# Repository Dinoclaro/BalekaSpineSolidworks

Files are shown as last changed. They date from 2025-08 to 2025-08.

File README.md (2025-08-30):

# Baleka Spine CAD Model

This repository contains the SolidWorks CAD model for the **Baleka Spine**.  
It is based on a modified version of the **Baleka 2.5 CAD** model, adapted for compatibility with both the new **three-degree-of-freedom (DoF) spine** and the existing **AeroDima tail**.

The Baleka Spine was developed to create a half-cheetah robotic model for studying the effect of the tail on the hindquarters during specific motions such as rapid turns. The spine integrates **three Steadywin GIM8115-6 motors** using MIT control to provide independent **roll**, **pitch**, and **yaw** actuation.  

The system is operated via **MATLAB Simulink Real-Time** on a **SpeedGoat** target computer.  

The design was created using **SolidWorks 2024 Student Edition**.  
All design calculations and resources are stored in the **BalekaSpine** folder within the NAS file system.

*Updated by Dino Claro ([clarodino@icloud.com](mailto:clarodino@icloud.com))*

## Manufacturing

- **Sheet metal parts**: Can be manufactured at Vulcan or Fabrinox. Specify required surface finishes and critical dimensions. The latest Baleka Spine assembly was manufactured at Vulcan.
- **Machined parts**: Can be produced at the Mechanical Engineering workshop.
- Refer to the **BOM** for a complete list of parts to be manufactured, 3D printed, or ordered.

## Assembly

- Refer to the **assembly instructions** doc.

## Shopping List

### 3-DOF Spine

| Part Number                                | Description                                                    | QTY | Supplier            |
|--------------------------------------------|----------------------------------------------------------------|-----|---------------------|
| BLKS-S001                                  | Heim Rod Turnbuckle                                            | 2   | Experimental Space  |
| Coiled Spring Pin Metric HD-4x35-St        | Coiled Spring Pin, Heavy Duty, 4 mm × 35 mm, Steel             | 3   | Topfast             |
| skf_bearing_6002-2rsh_2_01                 | SKF 6002-2RSH Deep Groove Ball Bearing                         | 3   | BMG                 |
| a_15_unstressed                            | 15 mm External Circlip                                         | 2   | BMG                 |
| skf_bearing_6001-2rsh_2_01                 | SKF 6001-2RSH Deep Groove Ball Bearing                         | 2   | BMG                 |
| B18.3.1M - 4 x 0.7 x 12 Hex SHCS -- 12NHX   | M4 × 12 mm Hex Socket Head Cap Screw                           | 24  | Topfast             |
| B18.3.4M - 4 x 0.7 x 8 SBHCS --N            | M4 × 8 mm Socket Button Head Cap Screw                         | 24  | Topfast             |
| AM-M4-N                                    | M4 Nyloc Nut                                                   | 38  | Topfast             |
| SHS4-8                                     | Socket Head Shoulder Screw                                     | 6   | Topfast             |
| Coiled Spring Pin Metric HD-3x28-St        | Coiled Spring Pin, Heavy Duty, 3 mm × 28 mm, Steel             | 1   | Topfast             |
| B18.3.1M - 4 x 0.7 x 30 Hex SHCS -- 20NHX   | M4 × 30 mm Hex Socket Head Cap Screw                           | 6   | Topfast             |
| skf_bearing_6003-2rsh_2_01                 | SKF 6003-2RSH Deep Groove Ball Bearing                         | 1   | BMG                 |
| B18.3.4M - 4 x 0.7 x 16 SBHCS --N           | M4 × 16 mm Socket Button Head Cap Screw                        | 3   | Topfast             |
| B18.3.1M - 4 x 0.7 x 35 Hex SHCS -- 20NHX   | M4 × 35 mm Hex Socket Head Cap Screw                           | 8   | Topfast             |
| a_17_unstressed                            | 17 mm External Circlip                                         | 1   | BMG                 |
| skf_bearing_6000-2rsh_2_01                 | SKF 6000-2RSH Deep Groove Ball Bearing                         | 2   | BMG                 |
| a_10_unstressed                            | 10 mm External Circlip                                         | 2   | BMG                 |
| B18.3.1M - 4 x 0.7 x 20 Hex SHCS -- 20NHX   | M4 × 20 mm Hex Socket Head Cap Screw                           | 3   | Topfast             |
| PHS 5 Body                                 | PHS5 Female Rod End Bearing Body                               | 4   | BMG                 |
| B18.3.1M - 5 x 0.8 x 20 Hex SHCS -- 20NHX   | M5 × 20 mm Hex Socket Head Cap Screw                           | 4   | Topfast             |
| 2020 V-Slot 3mtr Black                     | 20 × 20 mm Aluminium V-Slot Extrusion, 3 m, Black Anodised     | 4   | Moduasm             |
| T NUT PG15 PG20                            | T-Nut for 20 × 20 mm Extrusion Profile                         | 2   | Moduasm             |

---

## References

1. D. Bright, S. Shield, and A. Patel, "AeroDima: Cheetah-Inspired Aerodynamic Tail Design for Rapid Maneuverability," *2024 IEEE International Conference on Robotics and Automation (ICRA)*, Yokohama, Japan, 2024, pp. 1451–1456. [doi:10.1109/ICRA57147.2024.10610202](https://ieeexplore.ieee.org/document/10610202)  
2. C. Fischer, A. Blom, and A. Patel, “Baleka: A Bipedal Robot for Studying Rapid Maneuverability,” *Frontiers in Mechanical Engineering*, 2020. [doi:10.3389/fmech.2020.00054](https://www.frontiersin.org/articles/10.3389/fmech.2020.00054/full)

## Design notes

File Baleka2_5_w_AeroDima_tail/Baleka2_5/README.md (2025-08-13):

# Baleka 2.5 CAD Model

This is the SolidWorks CAD Model for Baleka 2.5. 

It was designed with SolidWorks 2024 Student Edition.

Updated by Matt Church

# Manufacturing + Assembly Tips
- Baleka 2.5 was originally manufactured using AL-1050 Aluminium, while structurally it is strong enough, the metal gets scuffed easily as it is softer. 
  It is recommended to use AL-5083 as it will show less visible wear and tear. 
- Plates can be manufactured at Vulcan of Fabrinox. Specify the surface finish or powder coating required.
  Needs to be collected if made at Vulcan. 
- Rear spacers are required for the motor mounting as the holes are blind, there is also not enough thread after the spacer for a 20mm M4 Cap screw to work. 
- A Half version can be made [Half_Leka]. This is created by using both outside plates and connecting them to a set of motors.

# Shopping List 

## Baleka Full 

| Item  | QTY   | Use   |
| :----- | :-----: | :----- |
| M4 x 20mm | 24 | Motor Front Mounting |
| M4 x 25mm | 24 | Motor Rear Mounting |
| M4 x 50mm | 24 | Connecting Legs to Motor |
| M5 x 14mm | 12 | Connecting top plate + Cross Braces |
| M5 x 10mm | 10 | Attaching items to Top Plate |
| M5 Nyloc | 8 | Connecting Top Plate | 

## Baleka Half [Half_Leka]

| Item  | QTY   | Use   |
| :----- | :-----: | :----- |
| M4 x 20mm | 12 | Motor Front Mounting |
| M4 x 25mm | 12 | Motor Rear Mounting |
| M4 x 50mm | 12 | Connecting Legs to Motor |
| M5 x 14mm | 8 | Connecting top plate + Cross Braces |
| M5 x 10mm | 5 | Attaching items to Top Plate |
| M5 Nyloc | 4 | Connecting Top Plate |

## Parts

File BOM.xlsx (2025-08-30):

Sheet: Supplied
 |  |  |  | BOM
 |  |  |  | Manufacturer Supplied
Part | Status | Supplier | Supplier link | Manufacturer | Part No. | Datasheet | Quantity | Price | Total Price
M5 Rod End Bearing, female, RH |  | BMG | https://bmgworld.net/bmg/en/ZAR/All-Categories/Bearings/Plain/Rod-Ends/Female-Thread/PHS-5/p/PHS%205 | IKO | PHS 5 | https://www.ikont.co.jp/global_data/download/pdf_catalog/cat5502dPHS.pdf | 4 | R 132.40 | R 529.59
5M Timing belt: 450 long, 15 wide, 90T | Ordered | RS-Components | https://za.rs-online.com/web/p/timing-belts/4750355 | Contitech | 450 5M 15 | https://docs.rs-online.com/6f9c/0900766b803c5d9d.pdf | 2 | R 264.48 | R 528.96
6001 2RS |  | BMG | https://bmgworld.net/bmg/en/ZAR/All-Categories/Bearings/Ball/Deep-Groove/Single-Row/6002-DDU/p/6002%20DDU | NSK | 6000 DDU |  | 2 | R 51.94 | R 103.88
6002 2RS |  | BMG | https://bmgworld.net/bmg/en/ZAR/All-Categories/Bearings/Ball/Deep-Groove/Single-Row/6003-DDU/p/6003%20DDU | NSK | 6002 DDU |  | 2 | R 57.54 | R 115.08
6003 2RS |  | BMG | https://bmgworld.net/bmg/en/ZAR/All-Categories/Bearings/Ball/Deep-Groove/Single-Row/6003-DDU/p/6003%20DDU | NSK | 6003 DDU |  | 2 | R 59.35 | R 118.70
Tente Swivel Castor Wheel, 40kg Capacity, 50mm Wheel |  | RS-Components | https://za.rs-online.com/web/p/castor-wheels/1721108?gb=s | Tente |  |  | 1 | R 165.05 | R 165.05
M3 Shoulder |  | Topfast |  |  |  |  | 5 | R 20.00 | R 100.00
M4 |  | Topfast |  |  |  |  | 50 | R 0.50 | R 25.00
M5 Bolts |  | Topfast |  |  |  |  | 15 | R 1.00 | R 15.00
 |  |  |  |  |  |  |  | TOTAL | R 1701.26
 | BMG
Part Name | Quantity | Price | Total
Spring Pin (3x28) | 1 | 2 | 2
Spring Pin (4x35) | 1 |  | 0
6001-2RSH | 2 | 51.94 | 103.88
6002-2RSH | 3 | 57.54 | 172.62
6000 -2RSH DGBB | 2 | 59.35 | 118.7
6003-2RSH-DGBB | 1 |  | 0
17mm Circlip | 1 |  | 0
15mm Circlip | 2 |  | 0
10mm Circlip | 2 |  | 0
M5 Rod End Bearing, Female, RH | 4 | 132.4 | 529.6
Bearing puller |  |  | 0
 |  |  | 0
 |  | TOTAL | 926.8
 | TOPFAST
Part Name | Quantity | Price | Total
Socket Head Shoulder (SHS) 4x30 | 2 | 10 | 20
Socket Head Cap Screw (SHCS) 4x12 | 24 | 2 | 48
Socket Button Head Cap Screw (SBHCS) 4x8 | 24 | 5 | 120
M4 Nut Nylock | 48 | 1 | 48
SHS 4x15 | 2 | 10 | 20
SHS 4x8 | 6 | 10 | 60
SHCS 4x30 | 6 | 5 | 30
SBHCS 4x12 | 8 | 5 | 40
SBHCS 4x16 | 3 | 5 | 15
SHCS 4x20 | 8 | 2 | 16
SHCS 4x20 | 3 | 2 | 6
loctite
2.5mm steel drill bit
Jigsaw blades
 |  | TOTAL | 423
 | Communica
lab wire <7
XT60
Soldering iron nibs
 | Mumbos
50L

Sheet: MechEng
 |  |  |  | Stress Analysis |  |  |  |  | Tolerances
Checked | Part | Quantity | Material | Yield Strength | Max Stress Expected | Safety Factor | Verification (Matlab or Solidworks) | Comments | Fits | Alignment
 | Machining
R | BLKS-M001-Diff_shaft_bearing_seat | 2 | AISI316 | 220 | 10 | 22 | SW | T_max = 25 Nm. This bearing seat experiences the largest loads. All other bearings seats assume similar stresses
R | BLKS-M002-Diff_shaft | 1 | AISI316 | 220 | 151 | 1.456953642 | Matlab | T_max = 25 Nm
R | BLKS-M003-Universal_joint_male | 1 | AL-5083-H116 | 228 | 59 | 3.86440678 | SW | T_max = 38Nm
R | BLKS-M004-Pulley_bearing_seat | 2 | ÀISI316 | 220 | 10 | 22
R | BLKS-M005-Roll_Bearing_6003 | 1 | AISI316 | 220 | 10 | 22
R | BLKS-M006-Roll_bearing_6002 | 1 | AISI316 | 220 | 10 | 22
R | BLKS-M007-Roll-Motor-Couple | 1 | AISI316 | 220 | N/A | 2.7 | SW | Assumes transmits torque like a key and is limited by shear strength. See Matlab script
Y | BLKS-M008-Universal_joint_female | 1 | AL-5083-H116 | 228 | 198 | 1.151515152 | Matlab | T_max = 38Nm. This applies a somewhat arbitrary shear stress concentration factor to account for the step introduced by the D-section and stresses are likely to be lower.
R | BLKS_M009-Universal_joint_shaft | 1 | AISI316 | 220 | 111 | 1.981981982 | Matlab | T_max = 38Nm

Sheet: Combined
PART NUMBER | DESCRIPTION | QTY | SUPPLIER | STATUS | STRESS |  |  |  | MATERIAL | PRICE (QTY X PPU) | COMMENTS
 |  |  |  |  | MAX STRESS | YIELD STRESS | SAFETY FACTOR | SOURCE
Manufactured
BLKS-M001 | DIff Shaft Bearing Seat | 2 | MechEng | A | 10 | 220 | 22.00 | SW | AISI316 |  |  | R | Ready, needs to be checked | RED
BLKS-M002 | Diff_shaft | 1 | MechEng | A | 151 | 220 | 1.46 | Matlab, Macsteel | AISI-316 |  |  | C | Checked | GREEN
BLKS-M003 | Universal Joint Male | 1 | MechEng | A | 59 | 250 | 4.24 | SW | AL6082 |  |  | O | Ordered | BLUE
BLKS-M004 | Pulley Bearing Seat | 2 | MechEng | A | 10 | 220 | 22.00 | SW | AISI-316 |  |  | A | Arrived | YELLOW
BLKS-M005 | Roll 6003 Seat | 1 | MechEng | A | 10 | 220 | 22.00 | SW | AISI-316
BLKS-M006 | Roll 6002 Bearing Seat | 1 | MechEng | A | 10 | 220 | 22.00 | SW | AISI-316
BLKS-M007 | Roll Motor Couple | 1 | MechEng | A | 140 | 220 | 1.57 | SW | AISI-316
BLKS-M008 | Universal Joint Female | 1 | MechEng | A | 198 | 250 | 1.26 | Matlab | AL6082
BLKS-M009 | Universal Joint Shaft | 1 | MechEng | A | 111 | 220 | 1.98 | Matlab | AISI-316
 |  |  |  |  |  |  |  |  |  | 0
Sheet Metal
BLKS-SM001 | Diff back plate | 1 | Vulcan | A |  |  |  |  | AL5182 |  | Check Surface finish, bend radius, material. Change 6mm to 5.8
BLKS-SM002 | Differential Side Plate Left Rib | 1 | Vulcan | A |  |  |  |  | AL5182
BLKS-SM003 | Diff Side Plate Shaft Right Rib | 1 | Vulcan | A |  |  |  |  | AL5182
BLKS-SM004 | Control Arm w Slot | 2 | Fabrinox | A |  |  |  |  | AL6082
BLKS-SM005 | Roll Plate | 1 | Vulcan | A |  |  |  |  | AL5182
BLKS-SM006 | Roll U-Plate | 1 | Vulcan | A |  |  |  |  | AL5182
BLKS-SM007 | Roll Support Plate | 1 | Vulcan | A |  |  |  |  | AL5182
BLKS-SM008 | Jockey Plate | 1 | Vulcan | A |  |  |  |  | AL5182
BLKS-SM009 | Differential Body Rib | 1 | Vulcan | O |  |  |  |  | AL5182
BLKS-SM010 | Roll Plate Frame | 1 | Vulcan | A |  |  |  |  | Stainless Steel
BLKS-SM011 | Motor Guard | 1 | Vulcan | A |  |  |  |  | AL5182
BLKS-SM012 | Tail Pitch Back | 1 | Vulcan | A |  |  |  |  | AL5182
BLKS-SM013 | Tail Pitch Front | 1 | Vulcan | A |  |  |  |  | AL5182
BLKS-SM014 | Tail Roll | 1 | Vulcan | A |  |  |  |  | AL5182
BLK-001 | Top Plate | 1 | Vulcan | A |  |  |  |  | Al5182 |  | 4mm thickness
 |  |  |  |  |  |  |  |  |  | 0
Printing
BLKS-P001 | Differential Shaft Pulley (PT-48T- 5M-15W-12B) | 2 |  |  |  |  |  |  | PLA
BLKS-P002 | Diff Motor Pulley (-PT-48T- 15W-12B) | 2 |  |  |  |  |  |  | PLA
BLKS-P003 | Universal Joint Rod End | 1 |  |  |  |  |  |  | PA-CF
BLKS-P004 | Control Rod End Back | 2 |  |  |  |  |  |  | PA-CF
BLKS-P005 | Control Rod End Front | 2 |  |  |  |  |  |  | PA-CF
BLKS-P007 | Roll Motor Spacer | 1 |  |  |  |  |  |  | PLA
BLKS-P008 | Tail Pitch Spacer | 1 |  |  |  |  |  |  | PLA
Supplied
BLKS-S001 | Heim Rod Turnbuckle | 2 | Experimental space | A |  |  |  |  |  | 0 | Found in experimental space
Coiled Spring Pin Metric HD-4x35-St | Coiled Spring Pin, Heavy Duty, 4 mm x 35 mm, Steel | 3 | Topfast | A |  |  |  |  |  | 8.88
skf_bearing_6002- 2rsh_2_01 | SKF 6002-2RSH Deep Groove Ball Bearing | 3 | BMG | A
a_15_unstressed | 15mm External Circlip | 2 | BMG | A
skf_bearing_6001- 2rsh_2_01 | SKF 6001-2RSH Deep Groove Ball Bearing | 2 | BMG | A
B18.3.1M - 4 x 0.7 x 12 Hex SHCS -- 12NHX | M4 x 12 mm Hex Socket Head Cap Screw | 24 | Topfast | A |  |  |  |  |  | 26.91
B18.3.4M - 4 x 0.7 x 8 SBHCS --N | M4 x 8 mm Socket Button Head Cap Screw | 24 | Topfast | A |  |  |  |  |  | 63.84
AM-M4-N | M4 Aluminium Spacer/Nut | 38 | Topfast | A |  |  |  |  |  | 41.42
SHS4-8 | Socket Head Shoulder Screw | 6 | Topfast | A
Coiled Spring Pin Metric HD-3x28-St | Coiled Spring Pin, Heavy Duty, 3 mm x 28 mm, Steel | 1 | Topfast | A |  |  |  |  |  | 2.28
B18.3.1M - 4 x 0.7 x 30 Hex SHCS -- 20NHX | M4 x 30 mm Hex Socket Head Cap Screw | 6 | Topfast | A
skf_bearing_6003- 2rsh_2_01 | SKF 6003-2RSH Deep Groove Ball Bearing | 1 | BMG | A
B18.3.4M - 4 x 0.7 x 16 SBHCS --N | M4 x 16 mm Socket Button Head Cap Screw | 3 | Topfast | A
B18.3.1M - 4 x 0.7 x 35 Hex SHCS -- 20NHX | M4 x 35 mm Hex Socket Head Cap Screw | 8 | Topfast | A
a_17_unstressed | 17mm External Circlip | 1 | BMG | A
skf_bearing_6000- 2rsh_2_01 | SKF 6000-2RSH Deep Groove Ball Bearing | 2 | BMG | A
a_10_unstressed | 10mm External Circlip | 2 | BMG | A
B18.3.1M - 4 x 0.7 x 20 Hex SHCS -- 20NHX | M4 x 20 mm Hex Socket Head Cap Screw | 3 | Topfast | A
PHS 5 Body | PHS5 Female Rod End Bearing Body | 4 | BMG | A
B18.3.1M - 5 x 0.8 x 20 Hex SHCS -- 20NHX | M5 x 20 mm Hex Socket Head Cap Screw | 4 | Topfast | A
2020 V-Slot 3mtr Black | 20x20 Aluminium V-Slot Extrusion, 3 m, Black Anodised | 4 | Moduasm | A |  |  |  |  |  | 143.33
T NUT PG15 PG20 | T-Nut for 20x20 Extrusion Profile | 2 | Moduasm | A

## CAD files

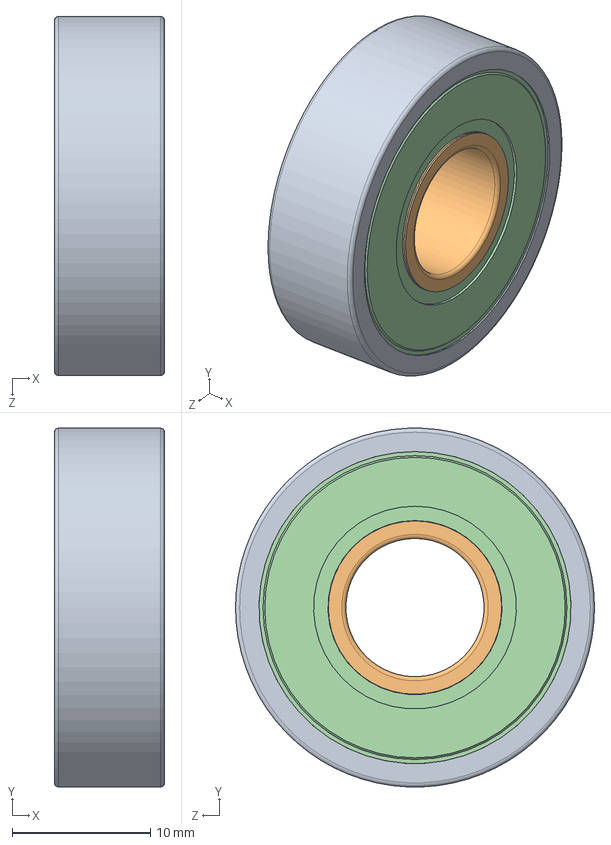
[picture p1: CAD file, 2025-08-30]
Supplied/skf_bearing_6000-2rsh_2/skf_bearing_6000-2rsh_2.SLDASM
8.00 x 26.0 x 26.0 mm
skf_bearing_6000-2rsh_2_01
skf_bearing_6000-2rsh_2_02
skf_bearing_6000-2rsh_2_03
skf_bearing_6000-2rsh_2_04
skf_bearing_6000-2rsh_2_05

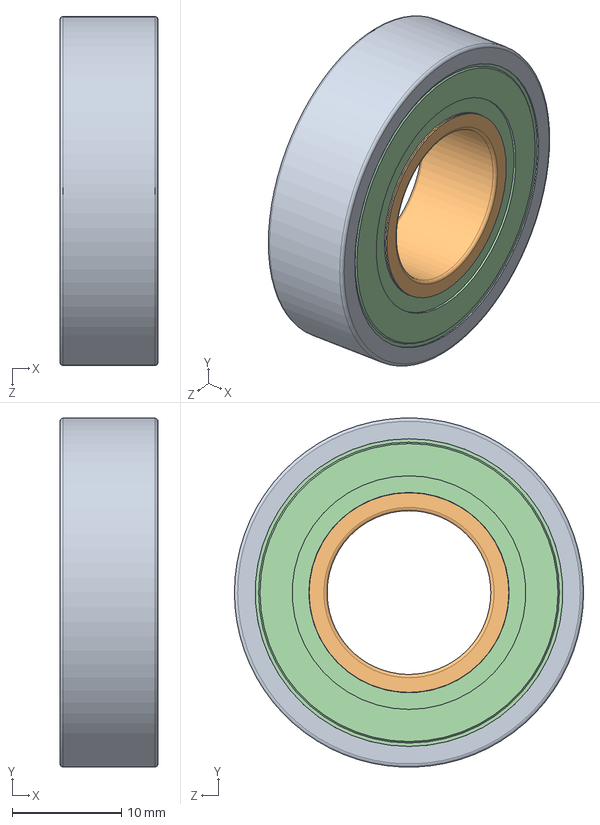
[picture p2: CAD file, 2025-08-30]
Supplied/skf_bearing_6002-2rsh_2/skf_bearing_6002-2rsh_2.SLDASM
9.00 x 32.0 x 32.0 mm
skf_bearing_6002-2rsh_2_01
skf_bearing_6002-2rsh_2_02
skf_bearing_6002-2rsh_2_03
skf_bearing_6002-2rsh_2_04
skf_bearing_6002-2rsh_2_05

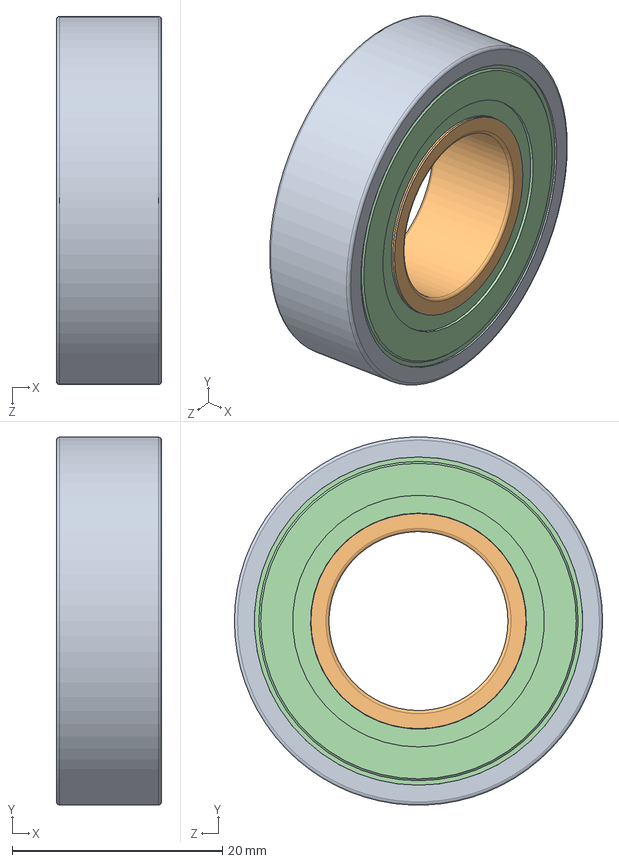
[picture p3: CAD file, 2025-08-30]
Supplied/skf_bearing_6003-2rsh_2/skf_bearing_6003-2rsh_2.SLDASM
10.0 x 35.0 x 35.0 mm
skf_bearing_6003-2rsh_2_01
skf_bearing_6003-2rsh_2_02
skf_bearing_6003-2rsh_2_03
skf_bearing_6003-2rsh_2_04
skf_bearing_6003-2rsh_2_05

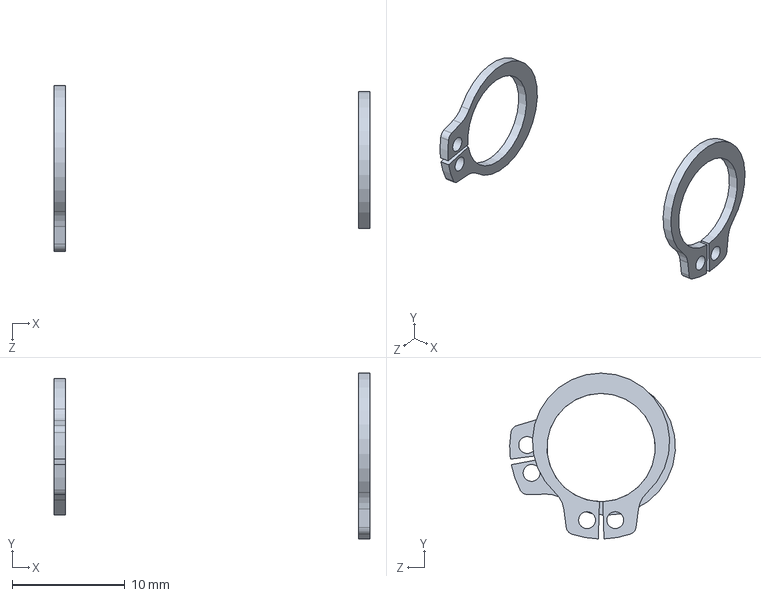
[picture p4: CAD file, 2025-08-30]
Baleka2_5_w_AeroDima_tail/Baleka2_5/Sub_Assemblies/AssemblyFootV2 BALEKA II .SLDASM
28.0 x 14.7 x 14.7 mm
circlip for shafts normal_din x 2

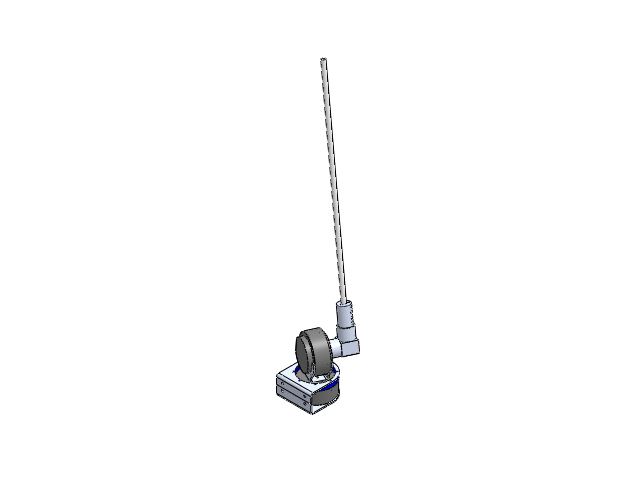
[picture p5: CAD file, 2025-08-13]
Baleka2_5_w_AeroDima_tail/Aero-dima_tail/Tail_assem.SLDASM
BLKS-SM012-tail-pitch-back
ak70-10 x 2
BLKS-SM014-tail_roll
roll spacer
tail_interface
carbon fiber tail
shaft coupler
BLKS-SM013-tail-pitch-front
BLKS-P008-tail-pitch-spacer

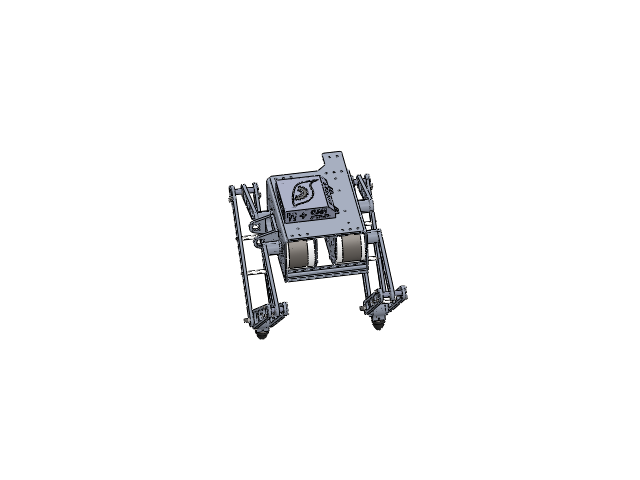
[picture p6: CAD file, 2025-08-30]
Baleka2_5_w_AeroDima_tail/Baleka2_5/Baleka2_5.SLDASM
AK10-9 KV60 V3.0 x 4
B2.5 Inner Shield Plate x 2
B2.5 Outer Shield Plate x 2
adapted_ring x 4
rear_ring x 4
rear_M4_spacer x 24
BLK001-top_plate
cross_brace x 2
Gland x 2
01-013 robot_mount_fixed
BLK2-002 Upper Leg Link New BALEKA II x 4
_6900_Outer_ring_2 BALEKA II x 12
_6900_Inner_ring_4 BALEKA II x 12
_6900_Ball_6 BALEKA II x 120
circlip for shafts normal_din x 20
BLK010 Middle Leg Joint Shaft New BALEKA II x 4
BLK009 Bearing Locator New BALEKA II x 8
socket head cap screw_iso x 16
BLK2-001 Upper Leg Coupler BALEKA II x 4
BLK2-003 Left Lower Leg Plated BALEKA II x 4
Lower Leg Compression Coupler BALEKA II x 8
BLK2-009 Inner Leg Pin BALEKA II x 8
plain washer 10673 type snl_iso x 16
hex thin nut gradeb_iso x 16
BLK2-004 Right Lower Leg Plated BALEKA II x 4
Spacer Lower Legs Link BALEKA II x 4
FootBlockDoubleBearing BALEKA II x 2
FootShaft BALEKA II x 2
FootRubber BALEKA II x 2
Baleka Lid v3.step
Leg_mount_spacer x 4
Cable_Bulkhead_mod

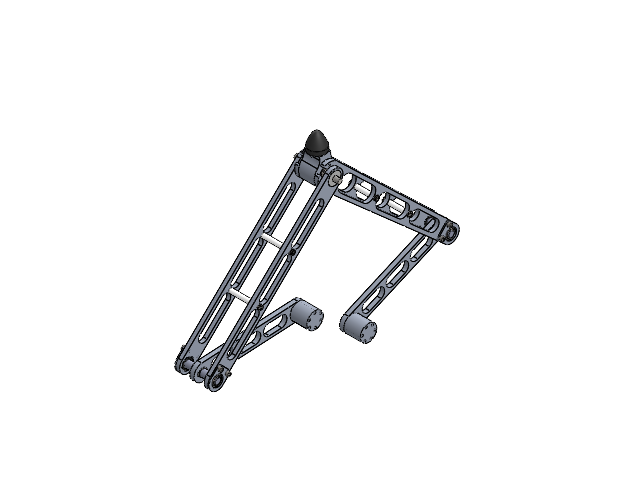
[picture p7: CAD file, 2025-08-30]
Baleka2_5_w_AeroDima_tail/Baleka2_5/Sub_Assemblies/Leg_pair.SLDASM
BLK2-002 Upper Leg Link New BALEKA II x 2
_6900_Outer_ring_2 BALEKA II x 6
_6900_Inner_ring_4 BALEKA II x 6
_6900_Ball_6 BALEKA II x 60
circlip for shafts normal_din x 10
BLK010 Middle Leg Joint Shaft New BALEKA II x 2
BLK009 Bearing Locator New BALEKA II x 4
socket head cap screw_iso x 8
BLK2-001 Upper Leg Coupler BALEKA II x 2
BLK2-003 Left Lower Leg Plated BALEKA II x 2
Lower Leg Compression Coupler BALEKA II x 4
BLK2-009 Inner Leg Pin BALEKA II x 4
plain washer 10673 type snl_iso x 8
hex thin nut gradeb_iso x 8
BLK2-004 Right Lower Leg Plated BALEKA II x 2
Spacer Lower Legs Link BALEKA II x 2
FootBlockDoubleBearing BALEKA II
FootShaft BALEKA II
FootRubber BALEKA II

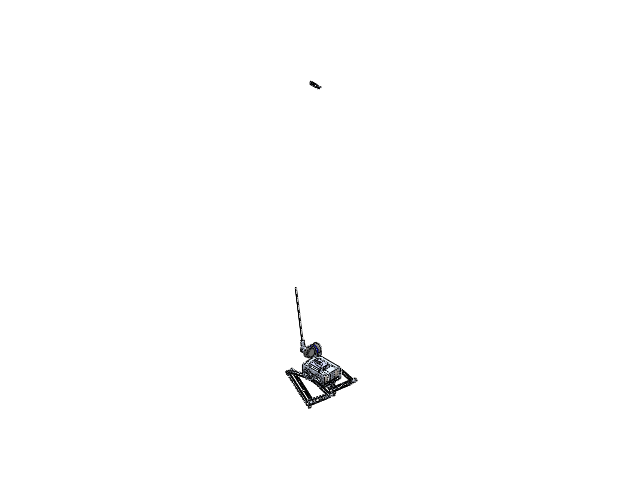
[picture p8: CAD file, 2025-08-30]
Baleka2_5_w_AeroDima_tail/baleka2_5_w_AeroDima_Tail.SLDASM
AK10-9 KV60 V3.0 x 4
B2.5 Inner Shield Plate x 2
B2.5 Outer Shield Plate x 2
adapted_ring x 4
rear_ring x 4
rear_M4_spacer x 24
BLK001-top_plate
cross_brace x 2
Gland x 2
01-013 robot_mount_fixed
BLK2-002 Upper Leg Link New BALEKA II x 4
_6900_Outer_ring_2 BALEKA II x 12
_6900_Inner_ring_4 BALEKA II x 12
_6900_Ball_6 BALEKA II x 120
circlip for shafts normal_din x 20
BLK010 Middle Leg Joint Shaft New BALEKA II x 4
BLK009 Bearing Locator New BALEKA II x 8
socket head cap screw_iso x 16
BLK2-001 Upper Leg Coupler BALEKA II x 4
BLK2-003 Left Lower Leg Plated BALEKA II x 4
Lower Leg Compression Coupler BALEKA II x 8
BLK2-009 Inner Leg Pin BALEKA II x 8
plain washer 10673 type snl_iso x 16
hex thin nut gradeb_iso x 16
BLK2-004 Right Lower Leg Plated BALEKA II x 4
Spacer Lower Legs Link BALEKA II x 4
FootBlockDoubleBearing BALEKA II x 2
FootShaft BALEKA II x 2
FootRubber BALEKA II x 2
Baleka Lid v3.step
Leg_mount_spacer x 4
Cable_Bulkhead_mod
BLKS-SM012-tail-pitch-back
ak70-10 x 2
BLKS-SM014-tail_roll
roll spacer
tail_interface
carbon fiber tail
shaft coupler
BLKS-SM013-tail-pitch-front
BLKS-P008-tail-pitch-spacer
PG20_Drop_Nut x 2
BLKS-P011-Back_plate_spacer x 2

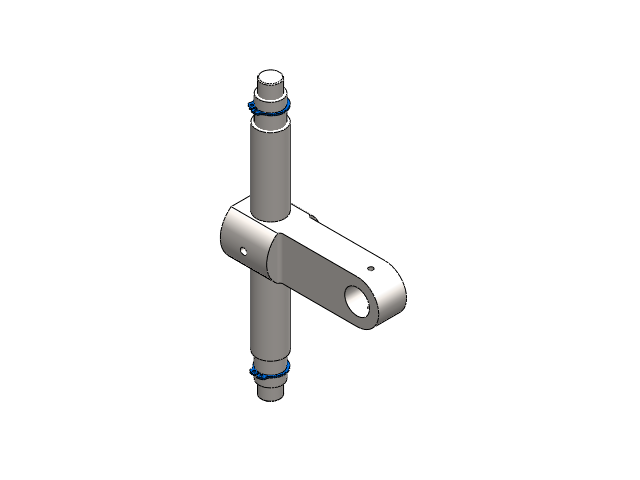
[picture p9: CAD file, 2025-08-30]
Sub-assemblies/diff_shaft_comp.SLDASM
BLKS-M002-diff_shaft
BLKS-M003-universal_joint_male
a_15_unstressed x 2

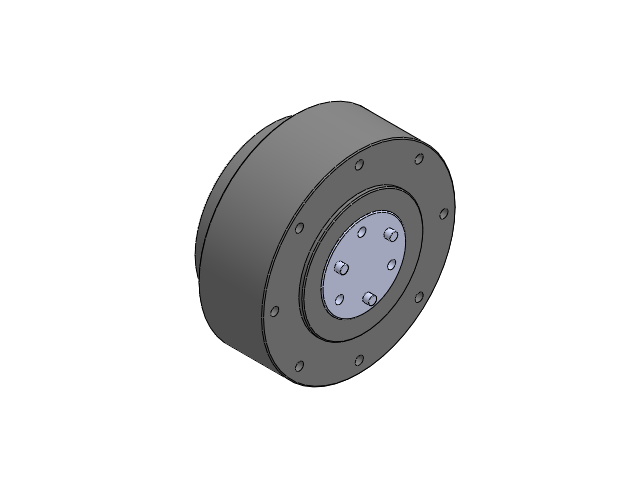
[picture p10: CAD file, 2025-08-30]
Supplied/GIM8115-6/motor_assem/motor_assem.SLDASM
motor_back_case
motor_shaft

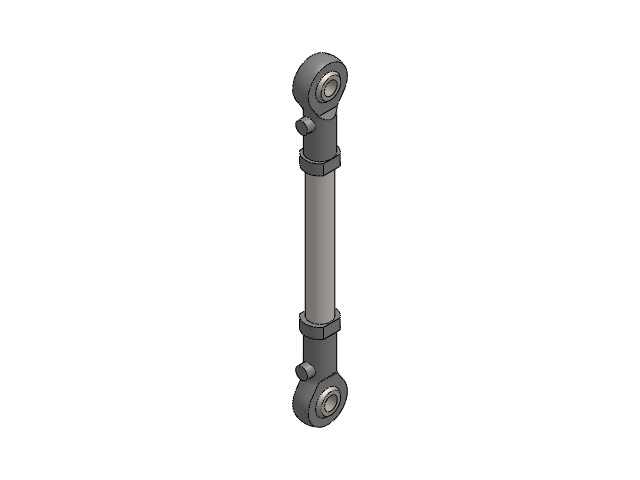
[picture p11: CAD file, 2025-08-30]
Supplied/Heim rod/heim_rod_assem.SLDASM
BLKS-S001-heim_rod_turnbuckle
PHS 5 BALL Copy x 2
PHS 5 Body x 2

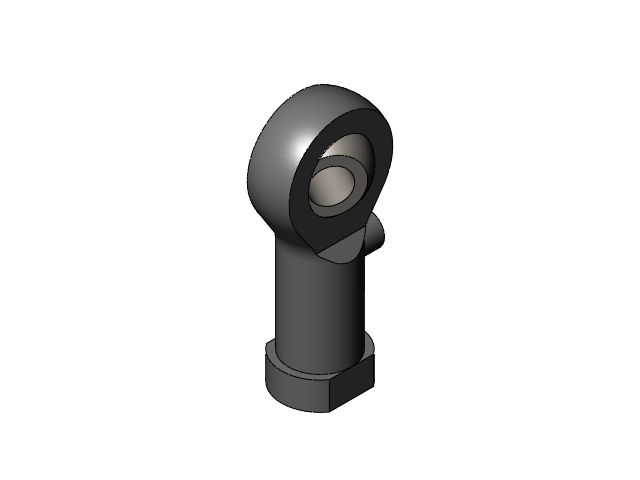
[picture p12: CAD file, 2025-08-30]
Supplied/IKO_PHS5A/SOLIDWORKS/PHS5A.sldasm
PHS 5 BALL Copy
PHS 5 Body

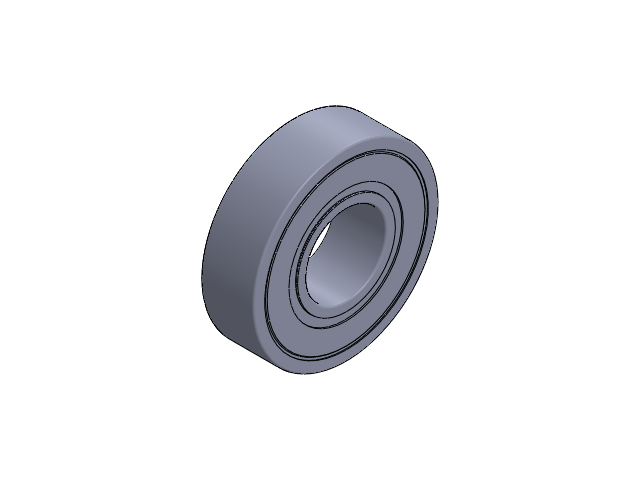
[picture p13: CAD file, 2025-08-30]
Supplied/skf_bearing_6001-2rsh_2/skf_bearing_6001-2rsh_2.SLDASM
skf_bearing_6001-2rsh_2_01
skf_bearing_6001-2rsh_2_02
skf_bearing_6001-2rsh_2_03
skf_bearing_6001-2rsh_2_04
skf_bearing_6001-2rsh_2_05

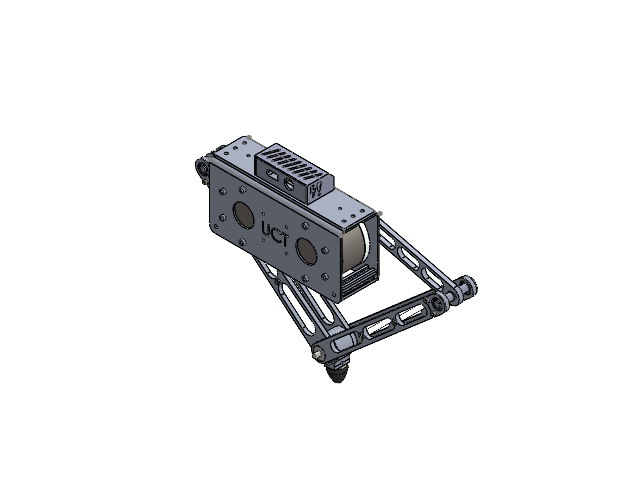
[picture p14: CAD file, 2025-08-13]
Baleka2_5_w_AeroDima_tail/Baleka2_5/Half_leka.SLDASM
adapted_ring x 2
AK10-9 KV60 V3.0 x 2
B2.5 Outer Shield Plate x 2
rear_ring x 2
Top_plate_half
BLK2-002 Upper Leg Link New BALEKA II x 2
_6900_Outer_ring_2 BALEKA II x 6
_6900_Inner_ring_4 BALEKA II x 6
_6900_Ball_6 BALEKA II x 60
circlip for shafts normal_din x 10
BLK010 Middle Leg Joint Shaft New BALEKA II x 2
BLK009 Bearing Locator New BALEKA II x 4
socket head cap screw_iso x 8
BLK2-001 Upper Leg Coupler BALEKA II x 2
BLK2-003 Left Lower Leg Plated BALEKA II x 2
Lower Leg Compression Coupler BALEKA II x 4
BLK2-009 Inner Leg Pin BALEKA II x 4
plain washer 10673 type snl_iso x 8
hex thin nut gradeb_iso x 8
BLK2-004 Right Lower Leg Plated BALEKA II x 2
Spacer Lower Legs Link BALEKA II x 2
FootBlockDoubleBearing BALEKA II
FootShaft BALEKA II
FootRubber BALEKA II
Cable_Bulkhead
Half-leka lid
cross_brace_half_leka x 2
rear_M4_spacer x 8

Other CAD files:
Baleka2_5_w_AeroDima_tail/Baleka2_5/Sub_Assemblies/Baleka_half.SLDASM
Sub-assemblies/eccentric_pulley_assem.SLDASM
Baleka2_5_w_AeroDima_tail/Baleka2_5/Sub_Assemblies/6900 BALEKA II .SLDASM
Sub-assemblies/diff_pulley_left_assem.SLDASM
Baleka2_5_w_AeroDima_tail/Aero-dima_tail/BLKS-P008-tail-pitch-spacer.SLDPRT
Baleka2_5_w_AeroDima_tail/Aero-dima_tail/BLKS-SM012-tail-pitch-back.SLDPRT
Baleka2_5_w_AeroDima_tail/Aero-dima_tail/BLKS-SM013-tail-pitch-front.SLDPRT
Baleka2_5_w_AeroDima_tail/Aero-dima_tail/BLKS-SM014-tail_roll.SLDPRT
Baleka2_5_w_AeroDima_tail/Aero-dima_tail/carbon fiber tail.SLDPRT
Baleka2_5_w_AeroDima_tail/Aero-dima_tail/roll spacer.SLDPRT
Baleka2_5_w_AeroDima_tail/Aero-dima_tail/shaft coupler.SLDPRT
Baleka2_5_w_AeroDima_tail/Aero-dima_tail/tail_interface.SLDPRT
Baleka2_5_w_AeroDima_tail/Baleka2_5/Drawings/B2.5 Inner Shield Plate.SLDDRW
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

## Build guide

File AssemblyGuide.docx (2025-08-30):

# Baleka Spine V1 Assembly Guide

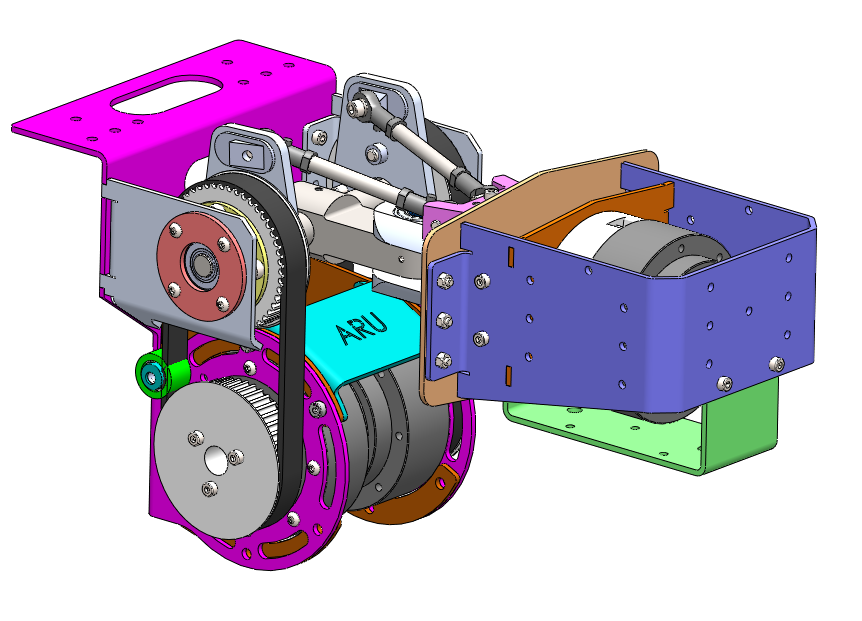
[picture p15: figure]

Updated by Dino Claro (26 August 2025)

All parts for the Spine, including the wiring harness, can be found in the project box. This guide aids with assembling the Spine and attaching it to Baleka and the frame. A brief explanation of the wiring harness is also provided. The guide primarily shows the order of assembly, and it is recommended to have the Solidworks model open alongside.

The procedure for assembling the parts that require press fits, such as the universal joint and bearings seats, is not shown here since they are already assembled and should not be taken apart unless a part has failed.

Assembly Tips:

- Washers are not shown in this guide. The general rule of thumb is to put the washer on the side that is turning. Depending on the access to the part this may either be the nut or the bolt head.
- When there are multiple screws/bolts, first tighten gently by hand and then tighten each bolt/screw by alternating to opposite sides.
- Nylock nuts are to be used throughout the assembly

## Differential Drive

### Control Arm Assembly

There are two Control-arm assemblies for the left and right Heim-rods, respectively.

Left and Right Control Assembly

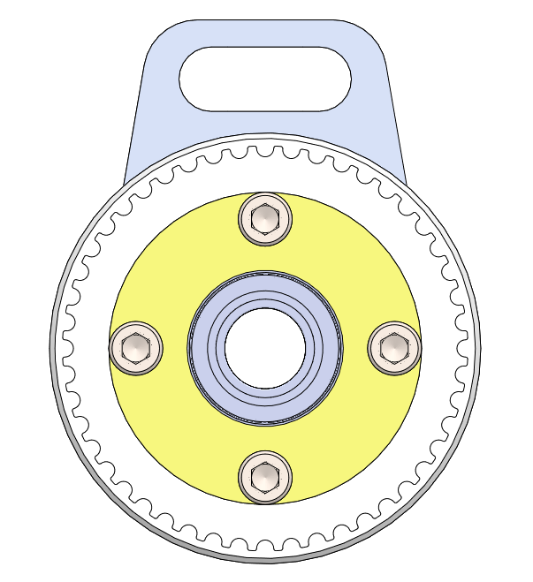
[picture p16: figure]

1. The 6002-Bearing Seat (BLKS-M004) slots into the cavity of the Differential Shaft Pulley (BLKS-P001) and is fastened with M6x30 shoulder screws and 3D printed washers (BLKS-P007).
2. Repeat for the other side.

### Differential Shaft

1. Fix the left and right control assemblies with 15mm circlips.

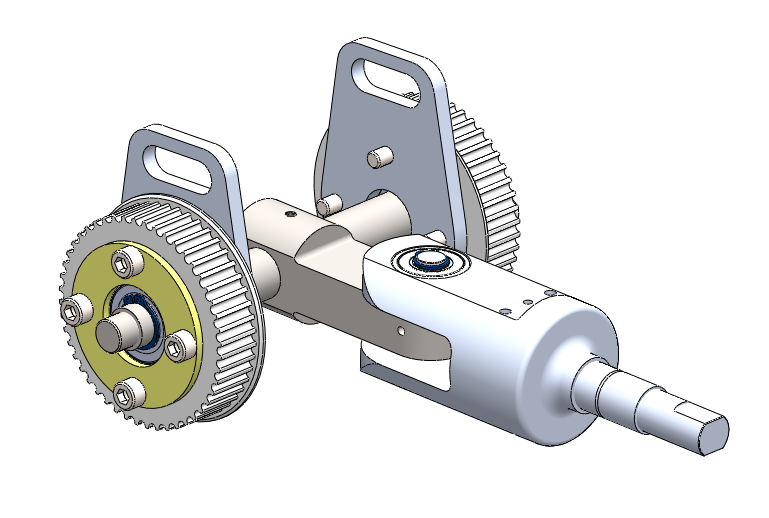
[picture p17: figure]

## Differential Drive Body

1. Attach the 6001-Bearing seat (BLKS-M001) to the side plates (BLKS-SM002 and BLKS-SM003) using M4x8 Button head screws. These screw directly into the side plates.
2. Fix the right-side Differential plate (BLKS-SM003) to the Differential back plate (BLKS-SM001) using M4x12 socket head cap screws.

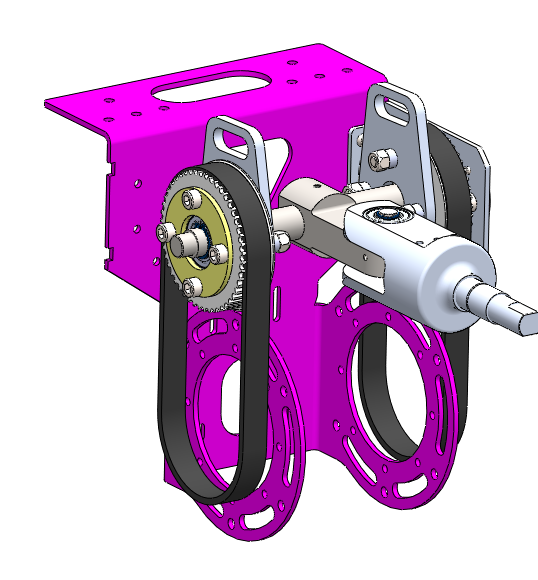
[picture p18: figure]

3. Manoeuvre the complete Differential Shaft assembly into the bearing of the right-side Differential plate. N.B. Timing belts should be placed on the pulleys at this point.

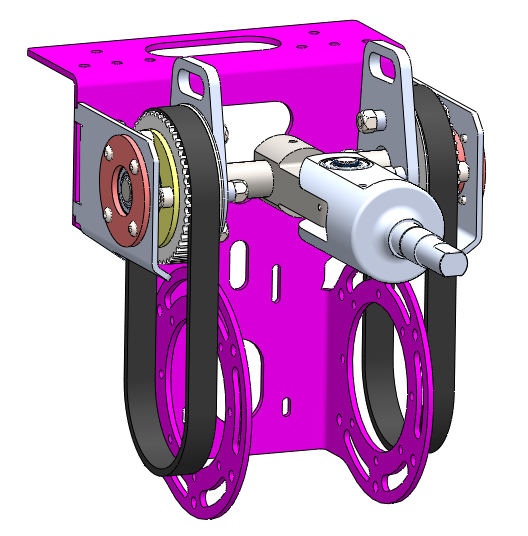
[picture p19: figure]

4. Slide the left-side Differential plate (BLKS-SM002) onto Differential Shaft and fix using M4x12 bolts. Take note of the bolt orientation for the left-side Differential plate in the image below. You should use a spanner to hold the nut and then tighten using the head of the bolt. The right-side bolt and nut can be in any orientation.
5. Place the Differential rib (BLKS-SM009) in-between the side plates of the Differential back plate (BLKS-SM001). The Differential Rib is fixed to the sides of Back-plate with M6x8 shoulder bolts.

Can included now for alignment but will have to be removed at a later stage when attaching Spine to Baleka

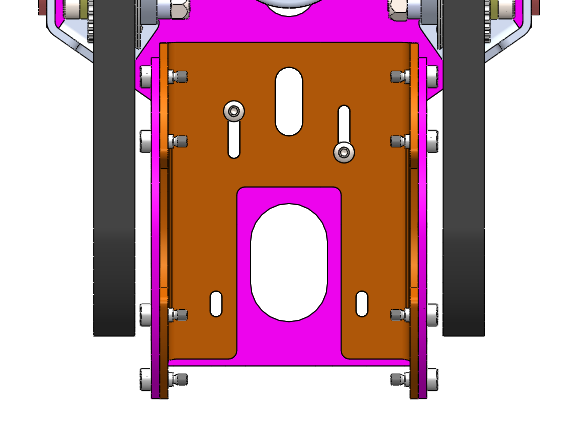
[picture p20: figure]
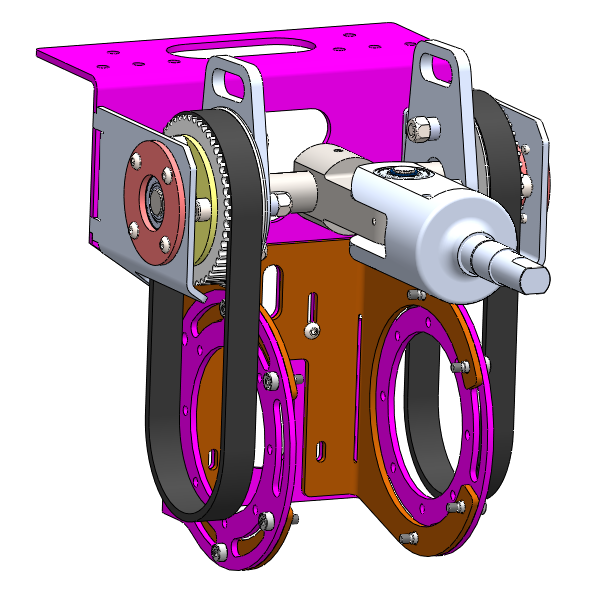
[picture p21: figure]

6. The Eccentric Belt Pulley tensioners are put together using various 3D printed parts (BLKS-P008, BLKS-P009 and BLKS-P010) as well as a 6800 DGBB. The tensioner assembly is attached to the Differential body using M6x35mm bolt and nut. Note: There may not be a hole in the Differential Rib. This is because the hole is too close to the bend line and must be drilled after receiving from Vulcan Steel. Insert the other shoulder bolts and mark the position with a drill punch to achieve correct hole location.

## Roll Body

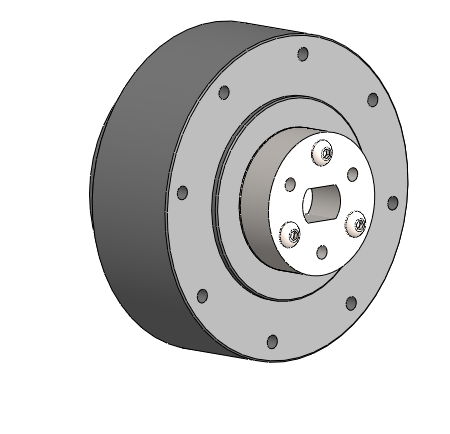
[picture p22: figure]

1. Attach Roll Motor Couple (BLKS-M007) to the GIM8115-6 Roll motor using M4x16 button head screws.

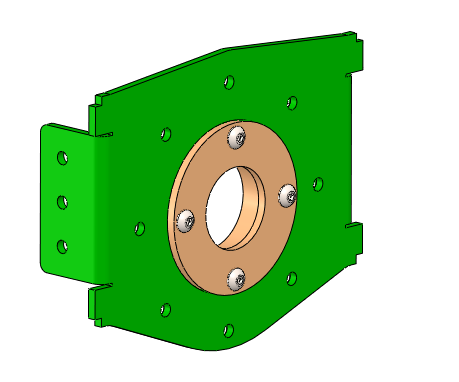
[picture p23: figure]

2. 6002 Bearing seat (BLKS-M006) attaches to Roll support plate (BLKS-SM007) with M4x12 button head bolts.
3. Attach the GIM8115-6 Motor to the Roll Support Plate using the Roll Motor Spacer (BLKS-P006) with M4x35 bolts.

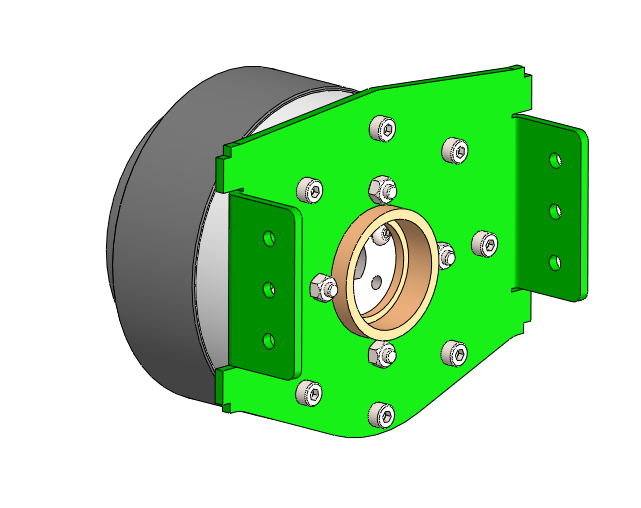
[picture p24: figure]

4. Slightly bend the Roll-U-Plate (BLKS-SM006) outwards for the tabs of the Roll support plate to slot in and attach the two sheet metal parts with M4x12mm bolts.

Roll Assembly

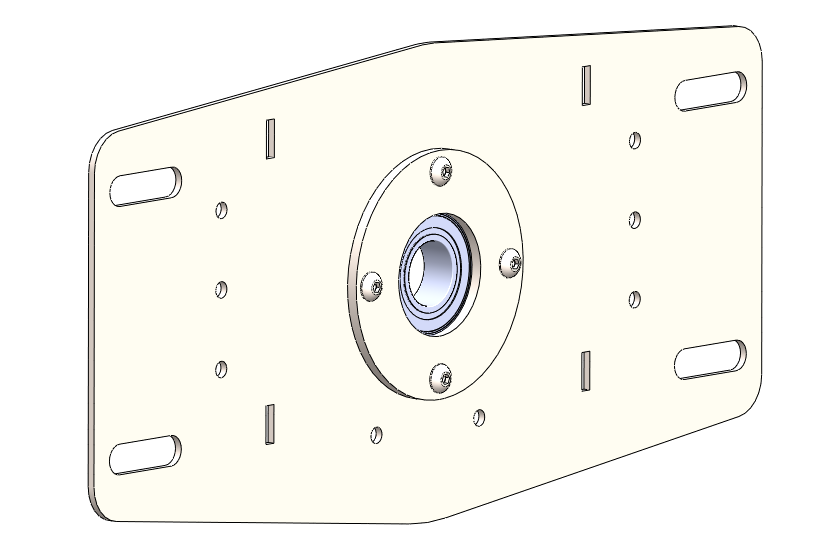
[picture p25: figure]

1. Slot the 6003 Bearing seat (BLKS-M005) into the Frame roll plate (BLKS-SM010) and fasten with M4x12 bolts.

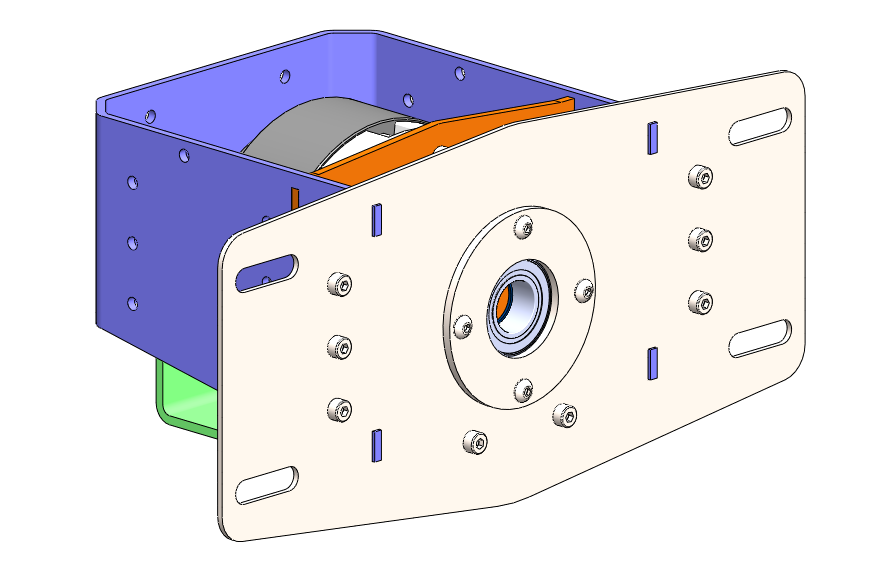
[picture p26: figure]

2. Align the Roll-U plate tabs with the slots of the Frame roll plate. This may require a bit of force. Use a rubber mallet at the back side of the U-plate. The sheet metal parts are fastened using M4x12 bolts.

## Spine Assembly

Roll Shaft

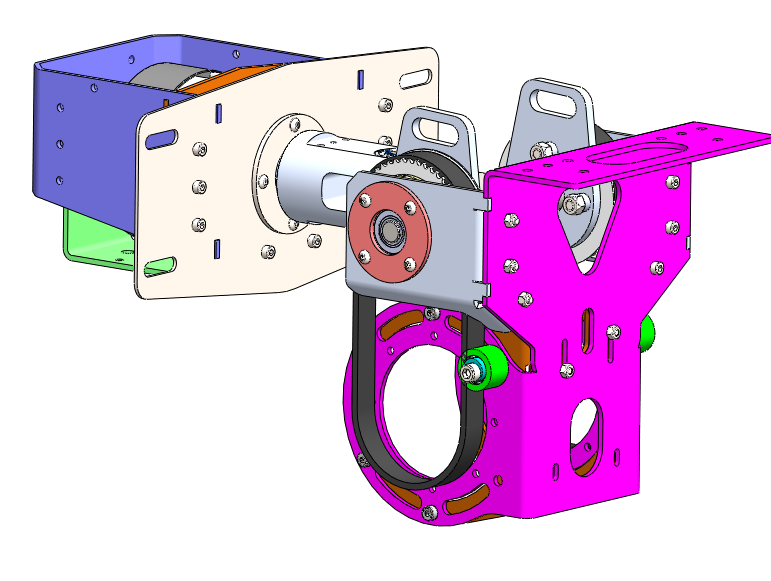
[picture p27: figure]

1. Slide the Universal-Joint female shaft into the Roll assembly. N.B.: Ensure that the 17 mm circlip is placed on the shaft before inserting it into the roll assembly. Initially, the circlip will slide along the smaller-diameter section of the shaft as it is inserted. Eventually, the circlip will need to be manually shifted along the shaft until it locates in the cavity. Tip: Check the orientation of the roll couple before sliding the shaft in.

17mm Circlip

## Frame

1. The spine attaches to two vertical extrusion profiles using 40x40 T-nuts (two for each side).

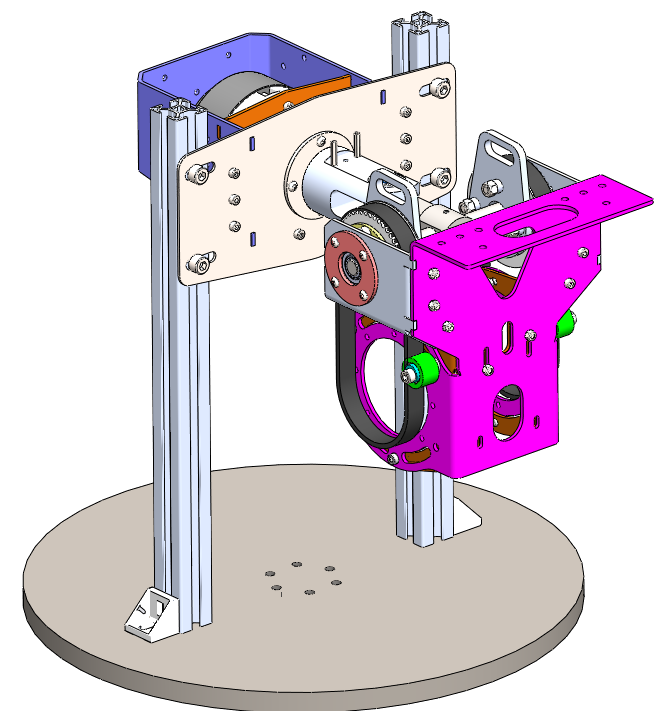
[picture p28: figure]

N.B. The extrusion that should be used is different from the CAD model. Use the 40x40 extrusion profiles from the experimental space to assemble the frame shown below.

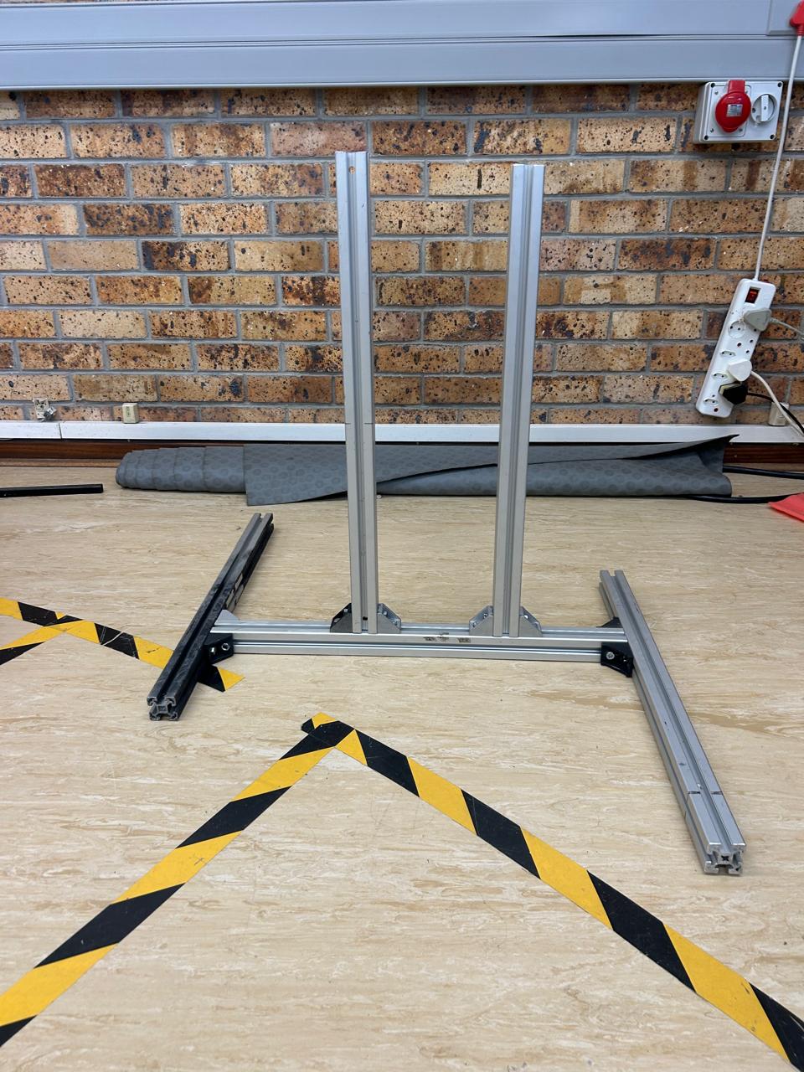
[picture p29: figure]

## Baleka

It is recommended to remove Baleka’s legs.

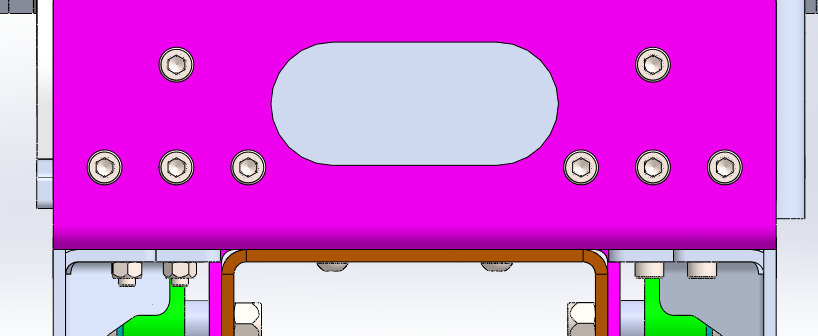
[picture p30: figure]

1. The Spine attaches to Baleka on the top plate using eight M5 bolts. Four of these are shared with the bolts that secure the two half-Balekas, two have dedicated threads in the top plate, and the remaining two fasten only the spine.

Top Side

To access the nut side of the bolts, the 20 × 20 mm extrusion profile must be removed. The nuts can then be tightened using a ratchet with an extension bar. If reaching the bolts proves difficult, a magnetic pen can help position the nuts.

Bottom Side

### Back Support

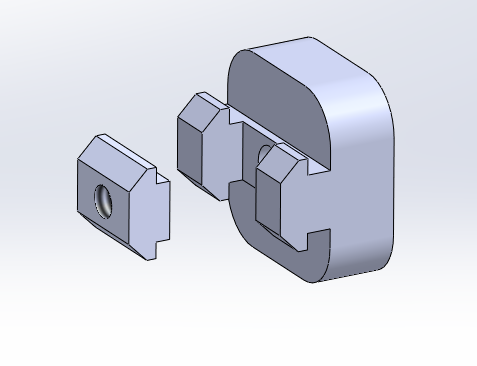
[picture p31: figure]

1. The Back plate of the spine is secured to the extrusion profile using a two custom 3D printed spacers (BLKS-P011). Parts are designed to interface with the 20x20 extrusion T-nuts that can be found in the experimental space supplies. N.B. These parts may not have been 3D printed yet.

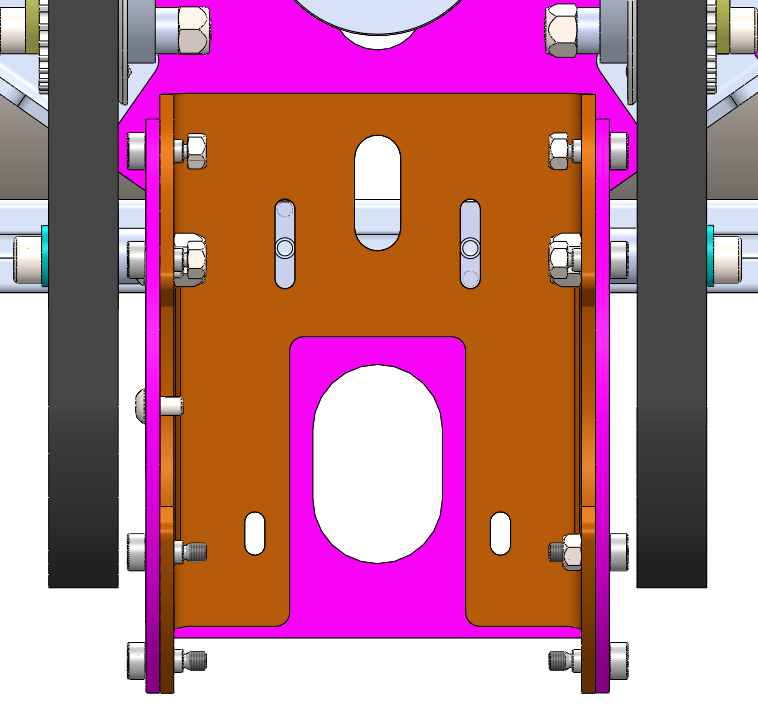
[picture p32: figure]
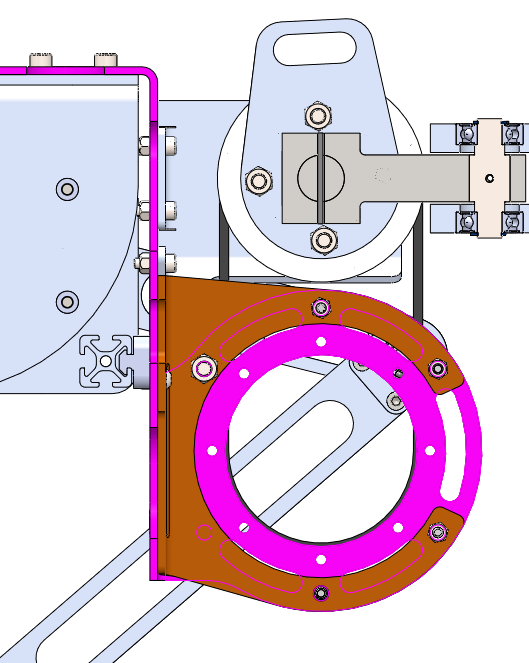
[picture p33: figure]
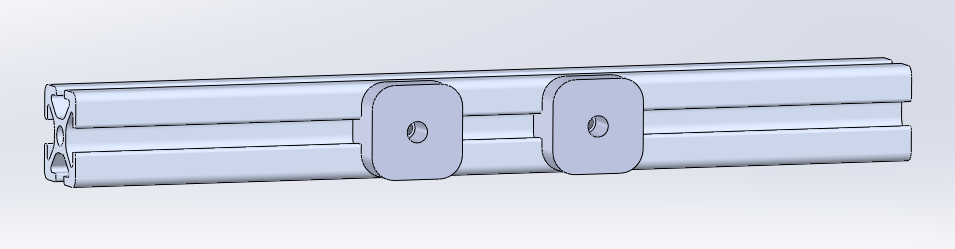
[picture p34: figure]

2. Slide the 3D-printed spacers and T-nuts into the extrusion profile. Reinstall the extrusion profile and secure the back plate to the extrusion profile with an M4 bolt running through the two vertical slots of the back plate, through the spacer, and into the T-nut.

## Control Arms

1. Slide the Universal Joint Rod End (BLKS-P003) over the two roll pins and secure with a M4x20 bolt.

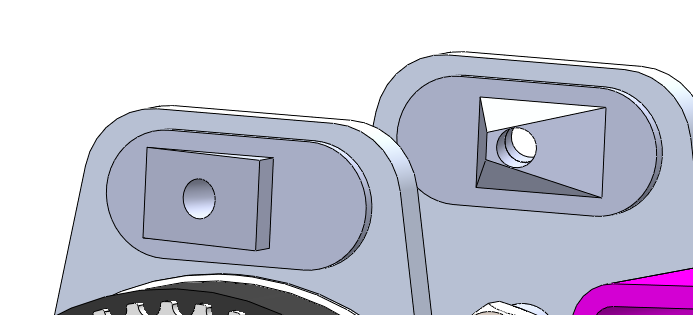
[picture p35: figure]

2. On each control arm, clip in the Control Rod End front and back (BLKS-P004 and BLKS-P005)
3. Note: The Heim-rod assembly looks different from the CAD model due to the decision to use turnbuckles. The Heim-rods are constructed with a turnbuckle, a left-hand thread, and a right-hand-thread rod-end bearing. The turnbuckle has a left-hand thread on one end and a right-hand thread on the other, allowing for easy adjustment. The rod-end bearings are attached to the 3D-printed parts (BLKS-P003/4/5) using M5×30 bolts. The 3D-printed rod-end parts are a work in progress, and further development is encouraged to improve the design for increased mobility and durability.

## Differential Motors

1. Attach the two Differential GIM8115-6 motors to the Differential back plate using M4x8 button head screws. N.B: Make sure the IO ports of the motors are facing up

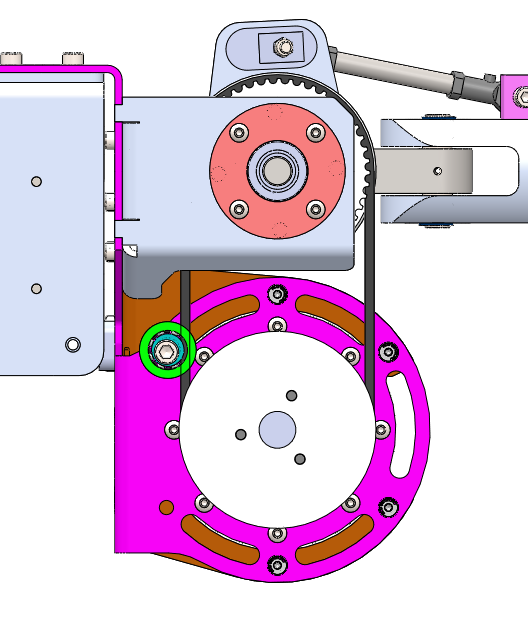
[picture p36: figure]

2. Align and slot the two Differential Motor Pulley (BLKS-P012) onto the Differential motors. This can be finicky ;(
3. N.B: Only complete this step are wiring is complete. Attach the two Motor guard (BLKS-SM011) using the M6 shoulder bolts. Note: The original design only has the top Motor guard. The updated design uses the second bottom motor guard.

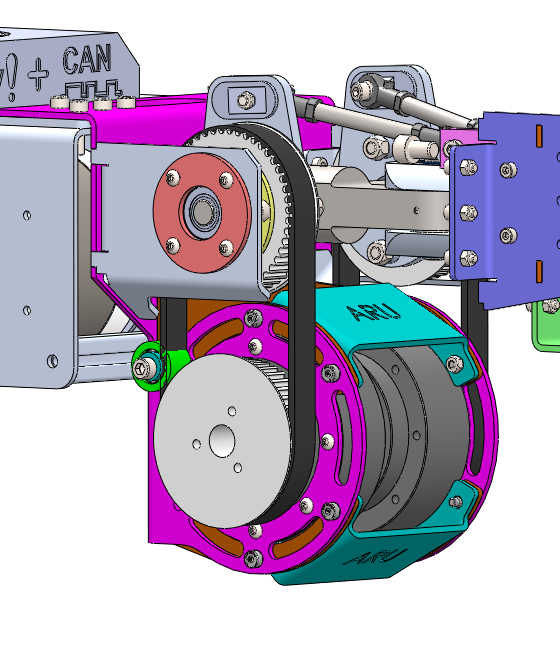
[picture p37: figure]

## Wiring

As of latest update of this document, the wiring harness has not been fully completed.

The existing wiring harness has the following power connections:

- XT90 to four XT30s: Baleka motors
- XT90 to two XT60s and a single XT30: Differential drive motors, tail motors, and roll motor
- XT90 to two XT90s: supplies the above adapters from the 3-phase 10 kW or single-phase 1.2 kW power supplies

To accommodate the nine CAN lines, a Veroboard is used, interfacing with the M16 connector running to the Speedgoat. The CAN lines from the various motors slot into the Veroboard as shown below:

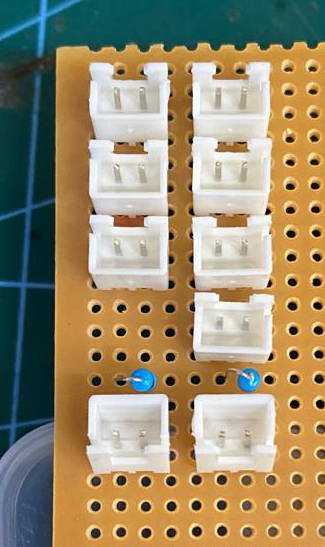
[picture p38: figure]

CAN Channel 1 (M16)

CAN Channel 2 (M16)

Tail Motors (2 lines)

Roll Motor

Differential Motors (2 lines)

Baleka Motors 1-4

Baleka Spine Assembly Guide26 August 2025V0

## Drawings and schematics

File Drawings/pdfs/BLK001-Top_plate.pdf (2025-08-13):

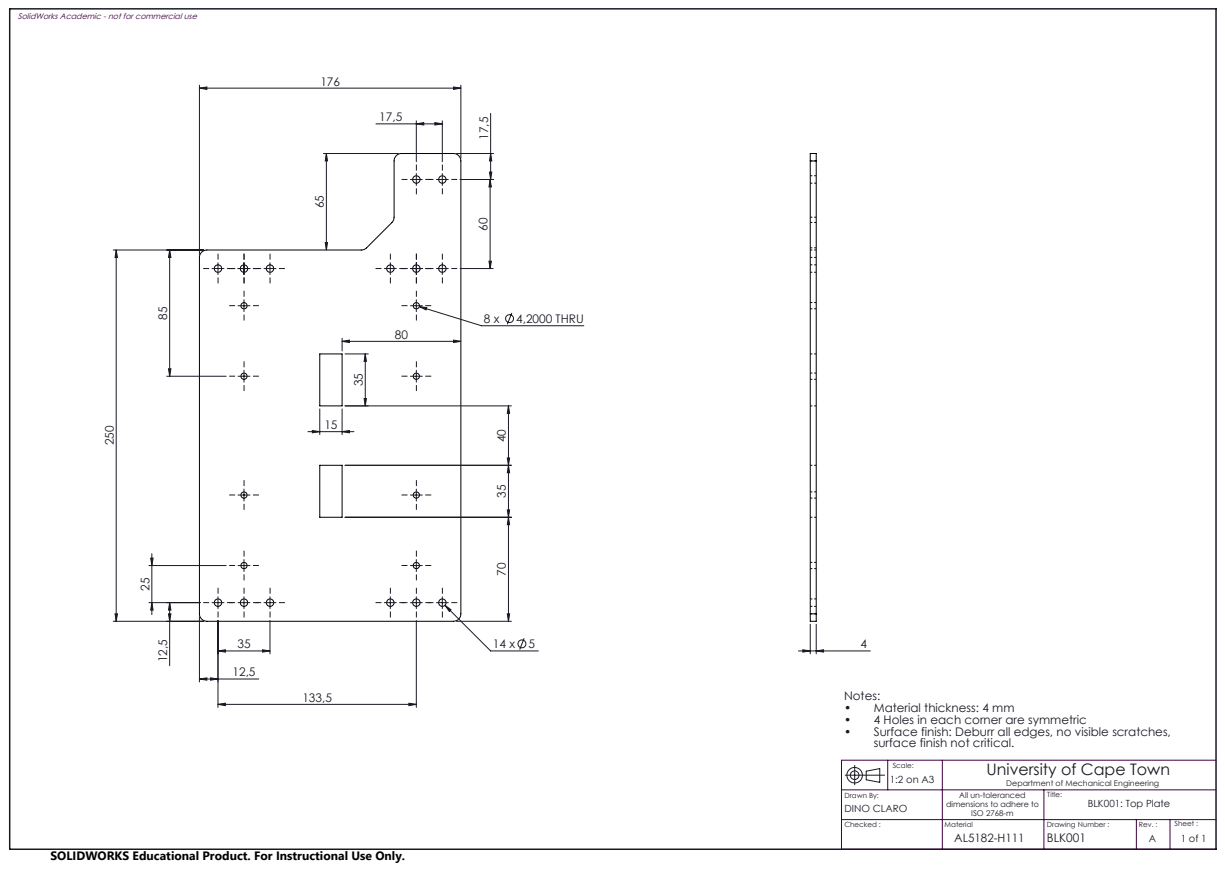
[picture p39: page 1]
8 x 4,2000 THRU

SolidWorks Academic - not for commercial use

Notes:
• Material thickness: 4 mm
• 4 Holes in each corner are symmetric
• Surface finish: Deburr all edges, no visible scratches,
surface finish not critical.

Scale: 1:2 on A3 | University of Cape Town Department of Mechanical Engineering

Drawn By: DINO CLARO | All un-toleranced dimensions to adhere to ISO 2768-m | Title: BLK001: Top Plate

Checked : | Material AL5182-H111 | Drawing Number : BLK001 | Rev. : A | Sheet :

SOLIDWORKS Educational Product. For Instructional Use Only.

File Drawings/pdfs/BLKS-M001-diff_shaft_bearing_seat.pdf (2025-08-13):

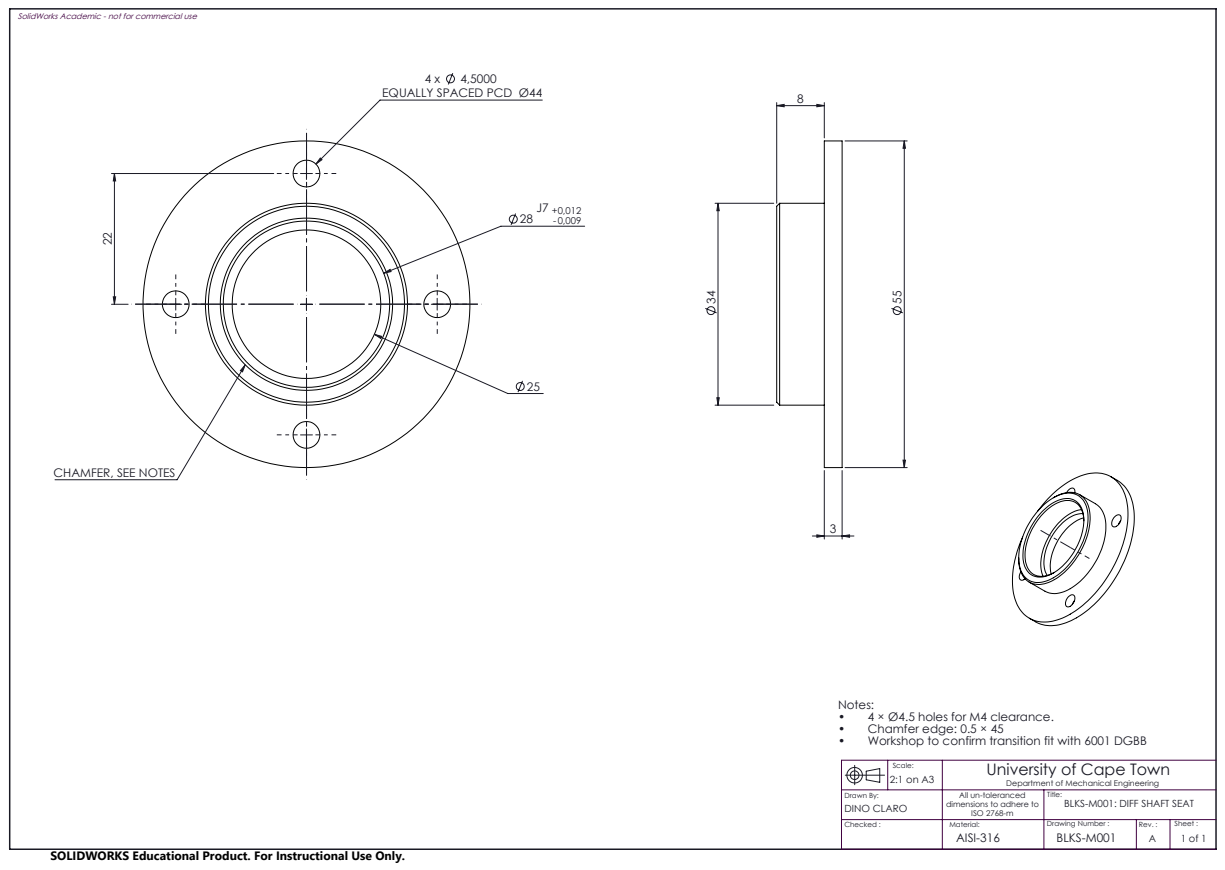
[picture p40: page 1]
4 × Ø4.5 holes for M4 clearance. •; Chamfer edge: 0.5 × 45

SolidWorks Academic - not for commercial use

EQUALLY SPACED PCD Ø44

CHAMFER, SEE NOTES

Notes:
• Workshop to confirm transition fit with 6001 DGBB

Scale: 2:1 on A3 | University of Cape Town Department of Mechanical Engineering

Drawn By: DINO CLARO | All un-toleranced dimensions to adhere to ISO 2768-m | Title: BLKS-M001: DIFF SHAFT SEAT

Checked : | Material: AISI-316 | Drawing Number : BLKS-M001 | Rev. : A | Sheet :

SOLIDWORKS Educational Product. For Instructional Use Only.

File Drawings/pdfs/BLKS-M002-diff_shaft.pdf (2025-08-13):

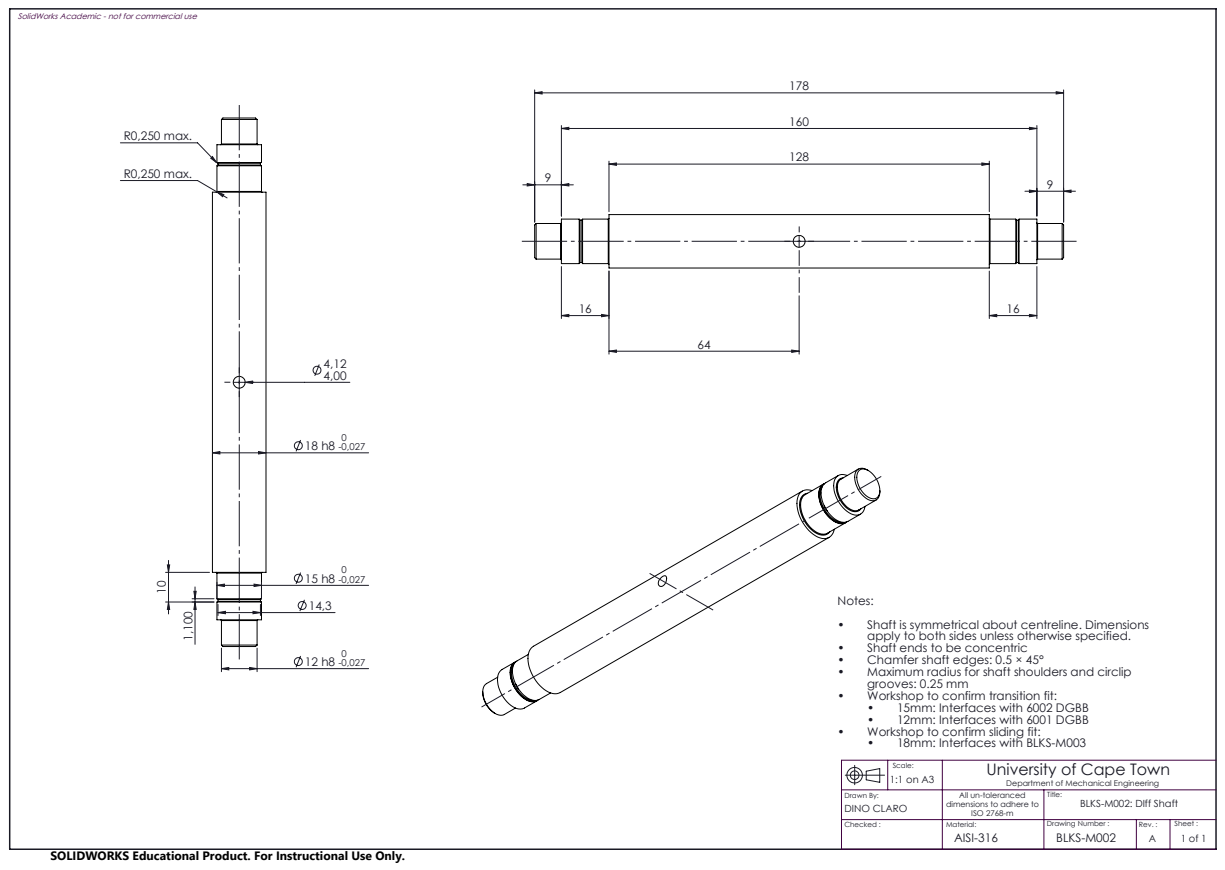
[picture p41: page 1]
R0,250 max.; Shaft ends to be concentric •; Chamfer shaft edges: 0.5 × 45°; grooves: 0.25 mm •; Workshop to confirm transition fit:; 12mm: Interfaces with 6001 DGBB •; Workshop to confirm sliding fit:

SolidWorks Academic - not for commercial use

Notes:
• Shaft is symmetrical about centreline. Dimensions
apply to both sides unless otherwise specified.
• Maximum radius for shaft shoulders and circlip
• 15mm: Interfaces with 6002 DGBB
• 18mm: Interfaces with BLKS-M003

Scale: 1:1 on A3 | University of Cape Town Department of Mechanical Engineering

Drawn By: DINO CLARO | All un-toleranced dimensions to adhere to ISO 2768-m | Title: BLKS-M002: DIff Shaft

Checked : | Material: AISI-316 | Drawing Number : BLKS-M002 | Rev. : A | Sheet :

SOLIDWORKS Educational Product. For Instructional Use Only.

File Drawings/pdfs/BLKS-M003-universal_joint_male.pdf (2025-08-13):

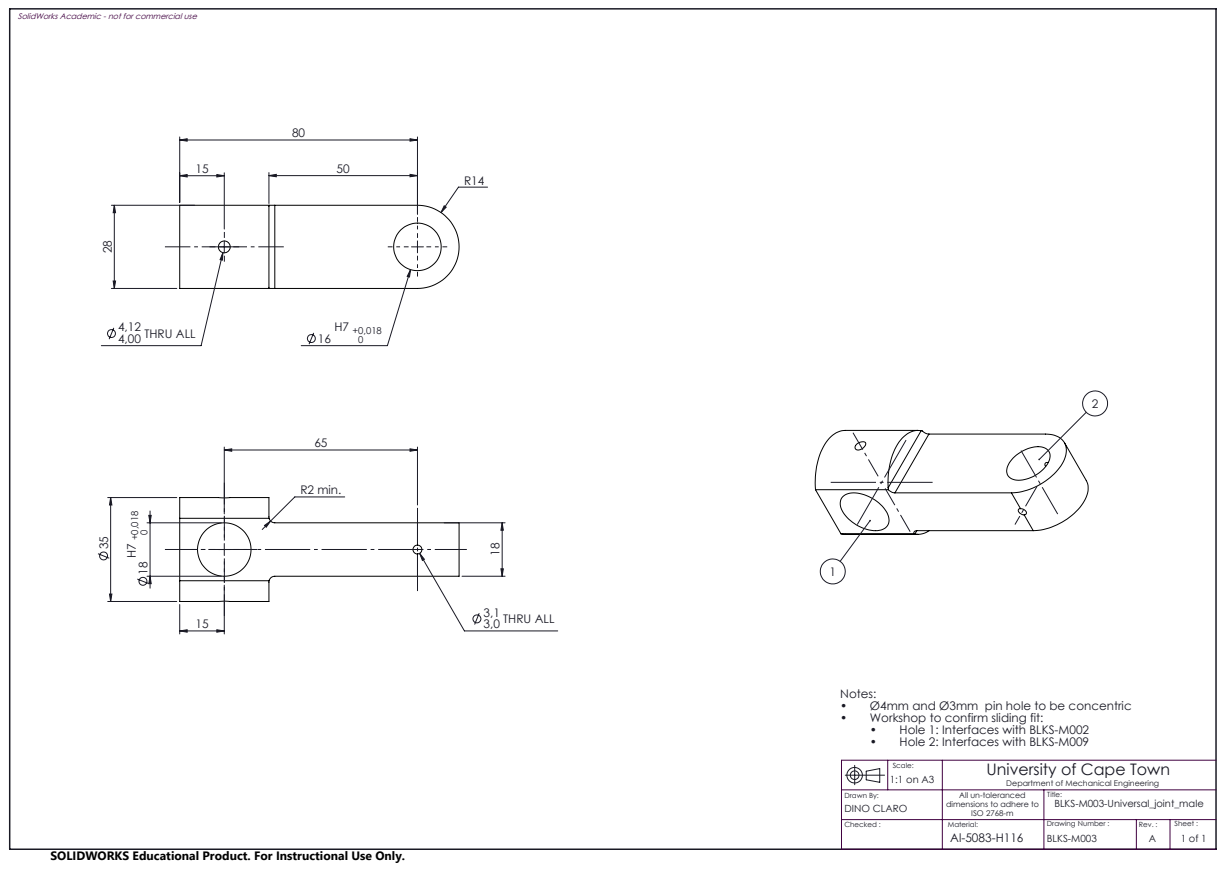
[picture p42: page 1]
4,00 THRU ALL; 3,0 THRU ALL 15; R2 min.

SolidWorks Academic - not for commercial use

Notes:
• Ø4mm and Ø3mm pin hole to be concentric
• Workshop to confirm sliding fit:
• Hole 1: Interfaces with BLKS-M002
• Hole 2: Interfaces with BLKS-M009

Scale: 1:1 on A3 | University of Cape Town Department of Mechanical Engineering

Drawn By: DINO CLARO | All un-toleranced dimensions to adhere to ISO 2768-m | Title: BLKS-M003-Universal_joint_male

Checked : | Material: Al-5083-H116 | Drawing Number : BLKS-M003 | Rev. : A | Sheet :

SOLIDWORKS Educational Product. For Instructional Use Only.

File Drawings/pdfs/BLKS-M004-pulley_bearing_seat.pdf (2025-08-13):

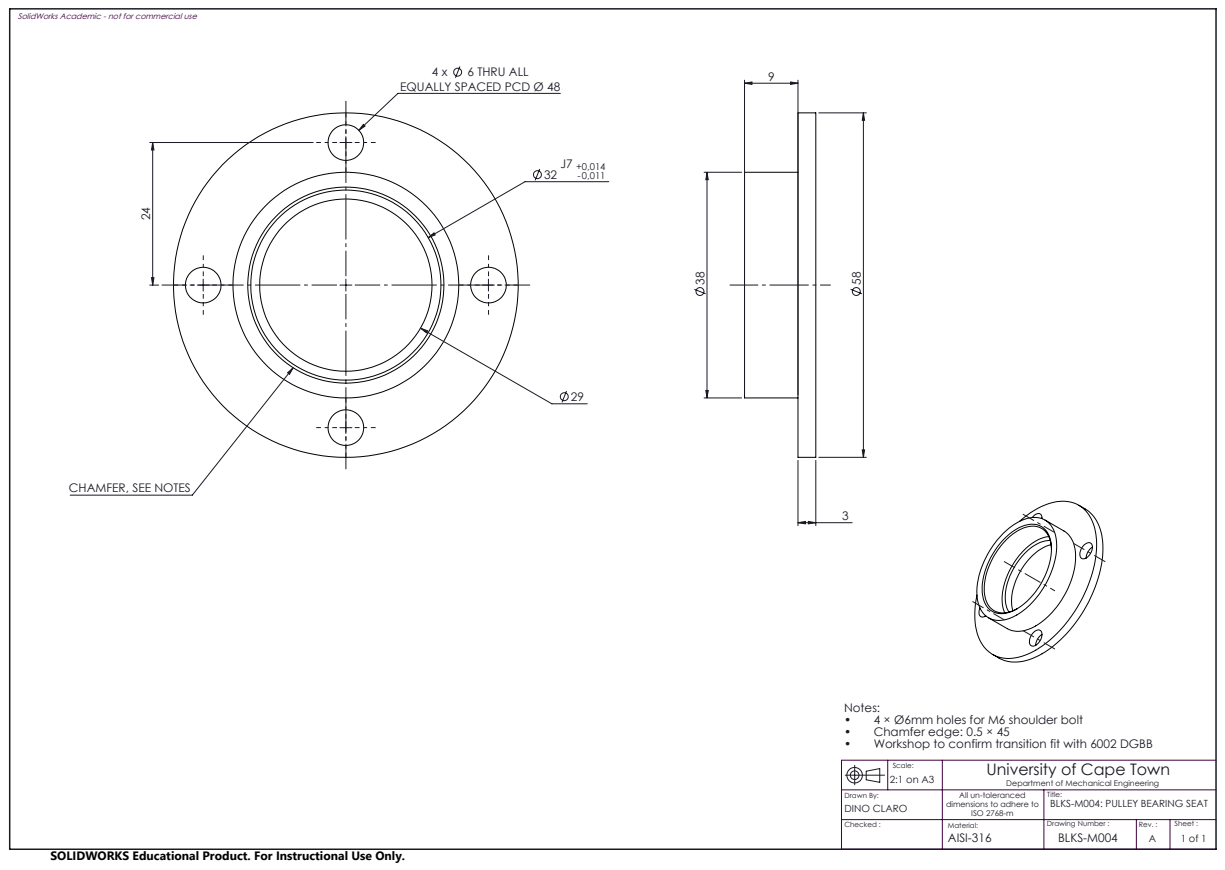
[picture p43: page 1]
6 THRU ALL; 4 × Ø6mm holes for M6 shoulder bolt •; Chamfer edge: 0.5 × 45 •; Workshop to confirm transition fit with 6002 DGBB

SolidWorks Academic - not for commercial use

EQUALLY SPACED PCD Ø 48

CHAMFER, SEE NOTES

Scale: 2:1 on A3 | University of Cape Town Department of Mechanical Engineering

Drawn By: DINO CLARO | All un-toleranced dimensions to adhere to ISO 2768-m | Title: BLKS-M004: PULLEY BEARING SEAT

Checked : | Material: AISI-316 | Drawing Number : BLKS-M004 | Rev. : A | Sheet :

SOLIDWORKS Educational Product. For Instructional Use Only.

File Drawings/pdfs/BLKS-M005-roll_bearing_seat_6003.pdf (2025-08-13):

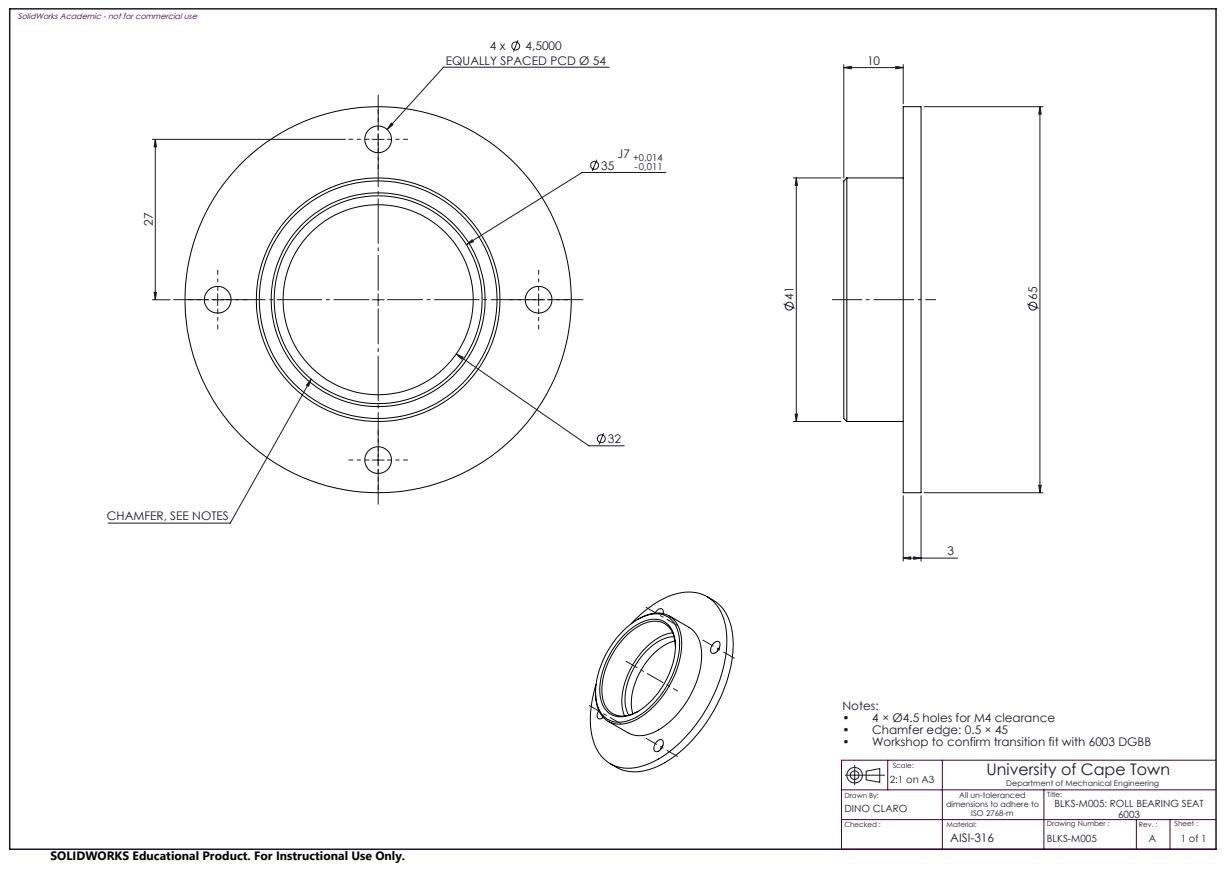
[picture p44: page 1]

SolidWorks Academic - not for commercial use

EQUALLY SPACED PCD Ø 54

CHAMFER, SEE NOTES

Notes:
• 4 × Ø4.5 holes for M4 clearance
• Chamfer edge: 0.5 × 45
• Workshop to confirm transition fit with 6003 DGBB

Scale: 2:1 on A3 | University of Cape Town Department of Mechanical Engineering

Drawn By: DINO CLARO | All un-toleranced dimensions to adhere to ISO 2768-m | Title: BLKS-M005: ROLL BEARING SEAT 6003

Checked : | Material: AISI-316 | Drawing Number : BLKS-M005 | Rev. : A | Sheet :

SOLIDWORKS Educational Product. For Instructional Use Only.

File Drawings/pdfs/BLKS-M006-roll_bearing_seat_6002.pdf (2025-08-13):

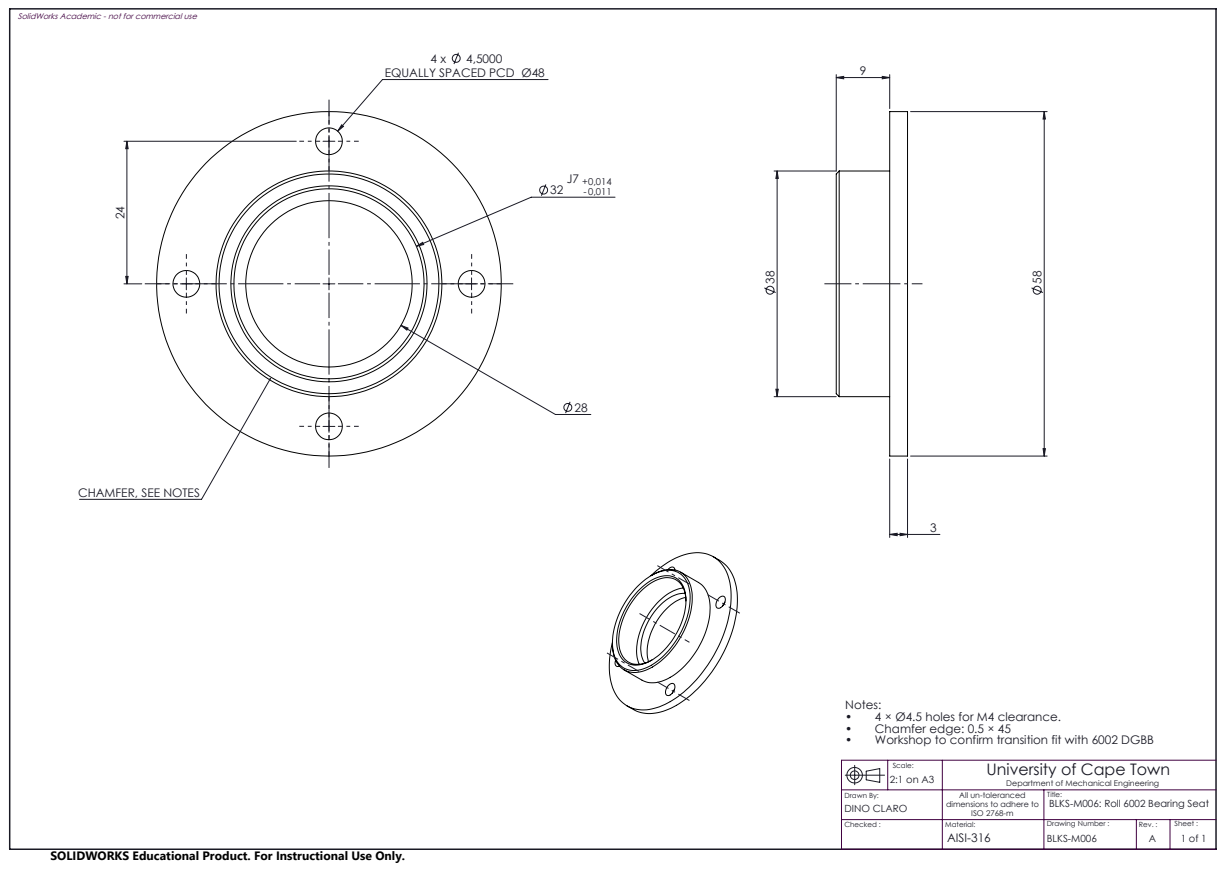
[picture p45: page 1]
Chamfer edge: 0.5 × 45 •; Workshop to confirm transition fit with 6002 DGBB

SolidWorks Academic - not for commercial use

EQUALLY SPACED PCD Ø48

CHAMFER, SEE NOTES

Notes:
• 4 × Ø4.5 holes for M4 clearance.

Scale: 2:1 on A3 | University of Cape Town Department of Mechanical Engineering

Drawn By: DINO CLARO | All un-toleranced dimensions to adhere to ISO 2768-m | Title: BLKS-M006: Roll 6002 Bearing Seat

Checked : | Material: AISI-316 | Drawing Number : BLKS-M006 | Rev. : A | Sheet :

SOLIDWORKS Educational Product. For Instructional Use Only.

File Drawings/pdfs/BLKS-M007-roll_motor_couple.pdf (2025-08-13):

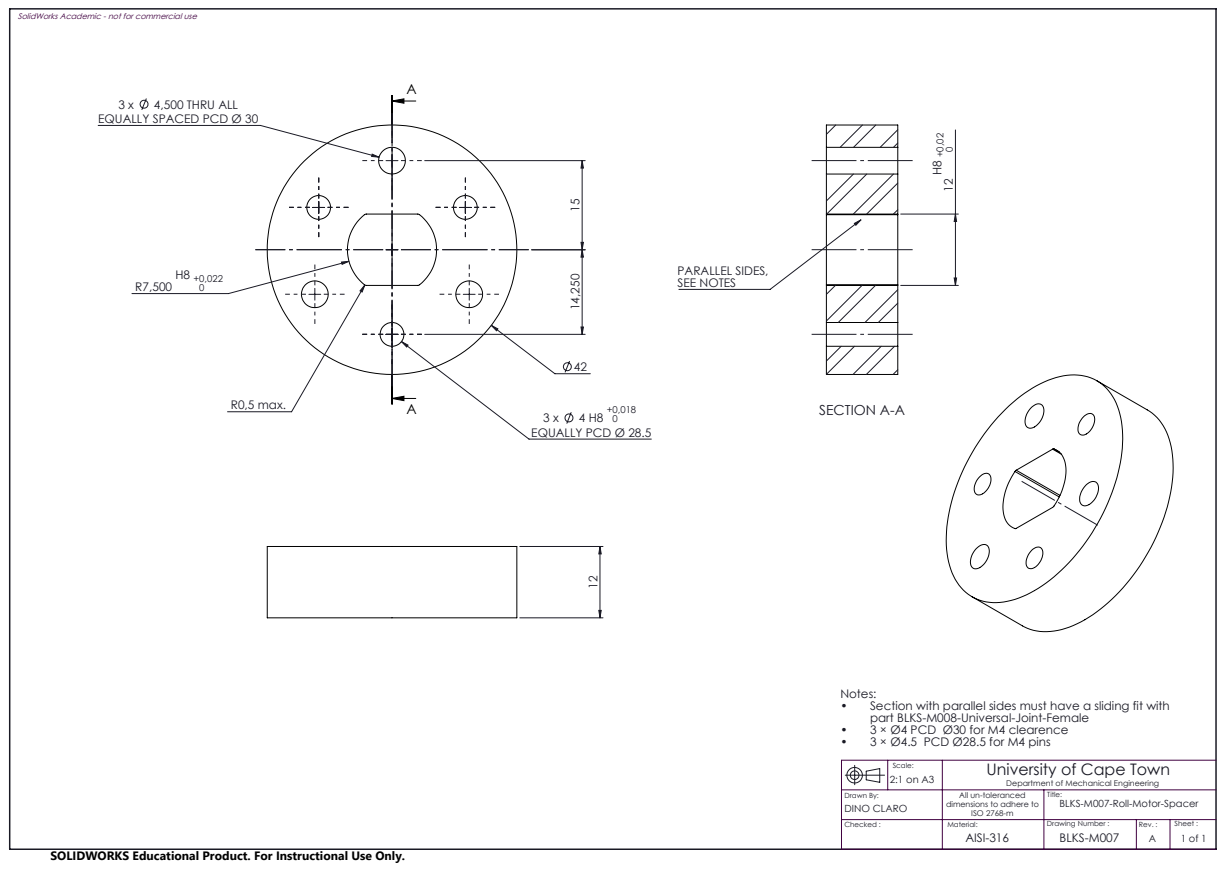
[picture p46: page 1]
4,500 THRU ALL; R0,5 max.; EQUALLY PCD Ø 28.5; SECTION A-A; PARALLEL SIDES, SEE NOTES; part BLKS-M008-Universal-Joint-Female •; 3 × Ø4 PCD Ø30 for M4 clearence

SolidWorks Academic - not for commercial use

EQUALLY SPACED PCD Ø 30

Notes:
• Section with parallel sides must have a sliding fit with
• 3 × Ø4.5 PCD Ø28.5 for M4 pins

Scale: 2:1 on A3 | University of Cape Town Department of Mechanical Engineering

Drawn By: DINO CLARO | All un-toleranced dimensions to adhere to ISO 2768-m | Title: BLKS-M007-Roll-Motor-Spacer

Checked : | Material: AISI-316 | Drawing Number : BLKS-M007 | Rev. : A | Sheet :

SOLIDWORKS Educational Product. For Instructional Use Only.

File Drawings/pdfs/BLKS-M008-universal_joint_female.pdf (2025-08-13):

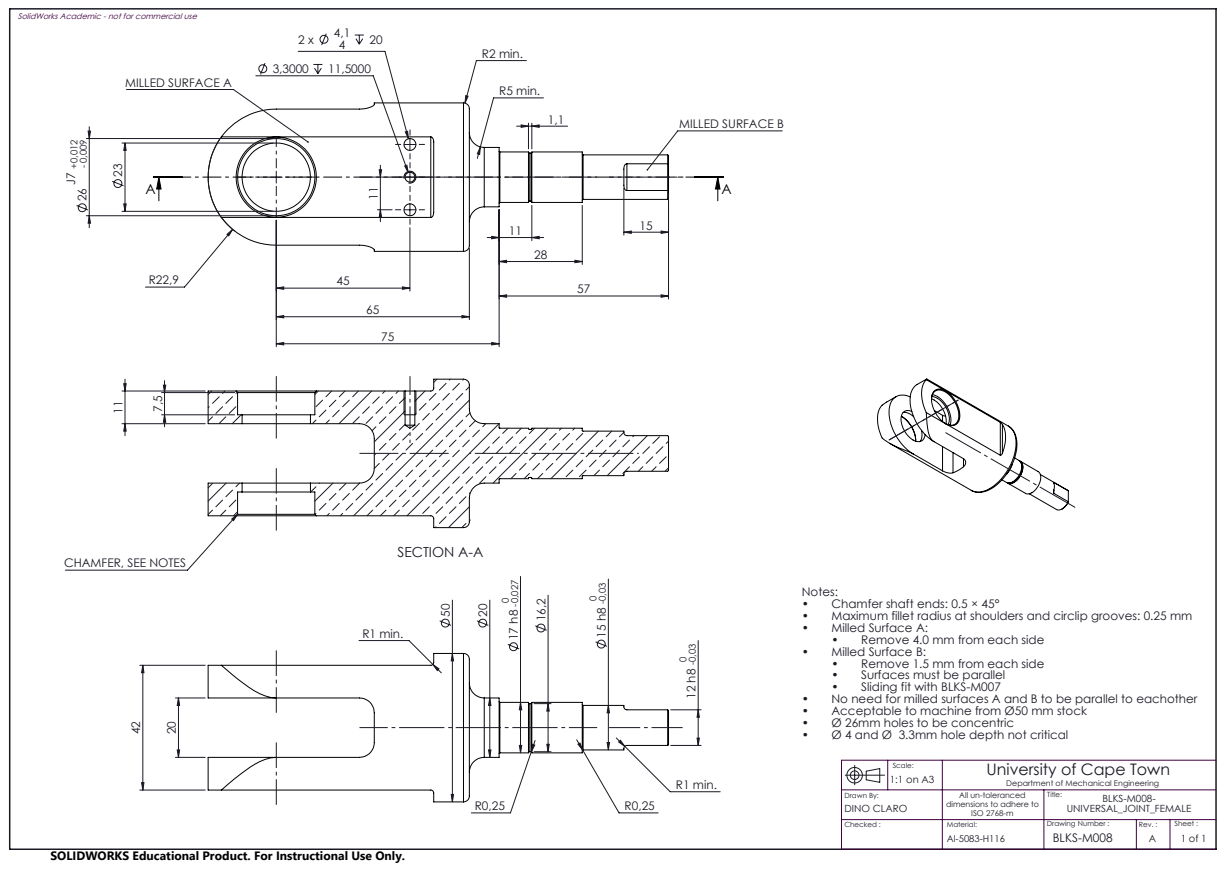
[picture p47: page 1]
R5 min.; R2 min.; MILLED SURFACE B; MILLED SURFACE A 42; R1 min.; SECTION A-A; Remove 1.5 mm from each side •; Surfaces must be parallel; Acceptable to machine from Ø50 mm stock •; Ø 26mm holes to be concentric

SolidWorks Academic - not for commercial use

CHAMFER, SEE NOTES

Notes:
• Chamfer shaft ends: 0.5 × 45°
• Maximum fillet radius at shoulders and circlip grooves: 0.25 mm
• Milled Surface A:
• Remove 4.0 mm from each side
• Milled Surface B:
• Sliding fit with BLKS-M007
• No need for milled surfaces A and B to be parallel to eachother
• Ø 4 and Ø 3.3mm hole depth not critical

Scale: 1:1 on A3 | University of Cape Town Department of Mechanical Engineering

Drawn By: DINO CLARO | All un-toleranced dimensions to adhere to ISO 2768-m | Title: BLKS-M008-UNIVERSAL_JOINT_FEMALE

Checked : | Material: Al-5083-H116 | Drawing Number : BLKS-M008 | Rev. : A | Sheet :

SOLIDWORKS Educational Product. For Instructional Use Only.

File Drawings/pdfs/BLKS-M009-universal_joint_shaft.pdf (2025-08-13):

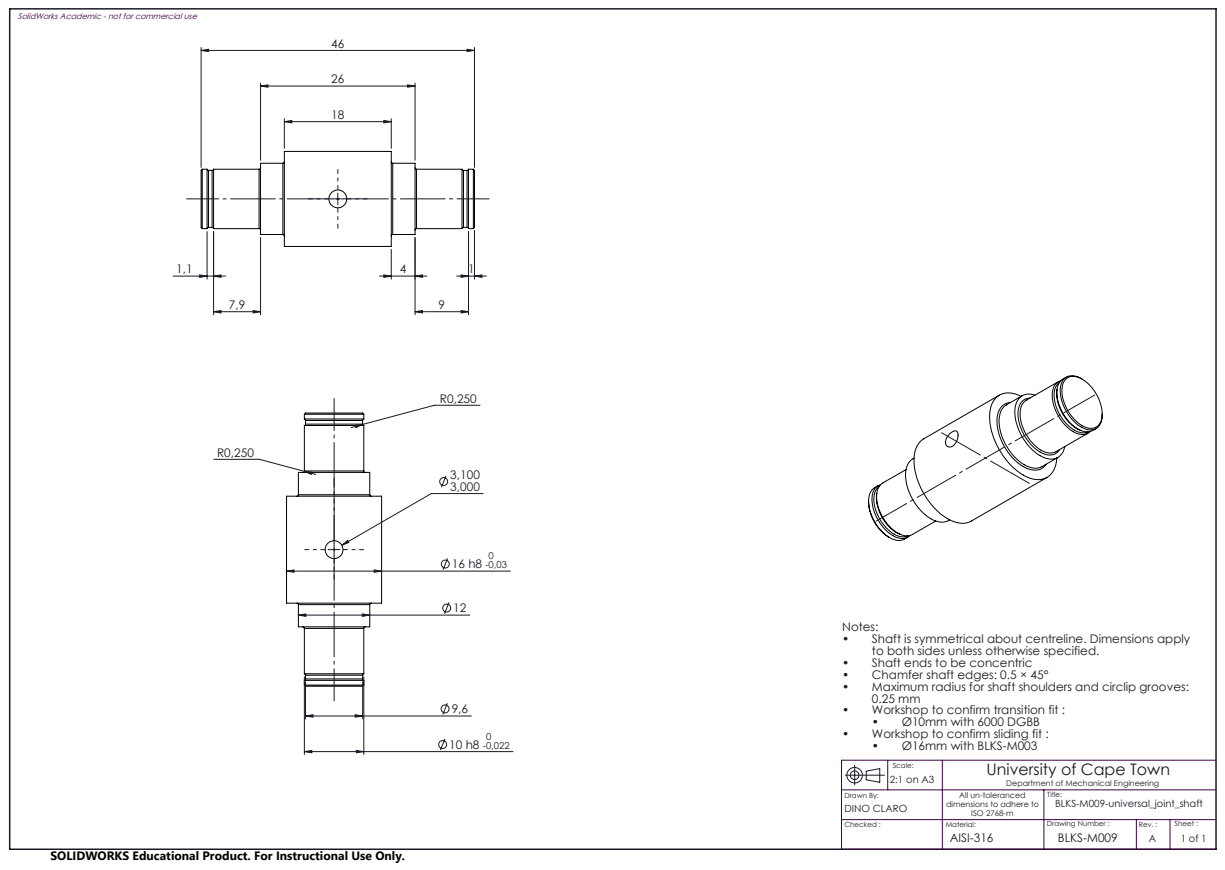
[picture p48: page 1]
Chamfer shaft edges: 0.5 × 45° •; Maximum radius for shaft shoulders and circlip grooves:

SolidWorks Academic - not for commercial use

Notes:
• Shaft is symmetrical about centreline. Dimensions apply
to both sides unless otherwise specified.
• Shaft ends to be concentric
• Workshop to confirm transition fit :
• Ø10mm with 6000 DGBB
• Workshop to confirm sliding fit :
• Ø16mm with BLKS-M003

Scale: 2:1 on A3 | University of Cape Town Department of Mechanical Engineering

Drawn By: DINO CLARO | All un-toleranced dimensions to adhere to ISO 2768-m | Title: BLKS-M009-universal_joint_shaft

Checked : | Material: AISI-316 | Drawing Number : BLKS-M009 | Rev. : A | Sheet :

SOLIDWORKS Educational Product. For Instructional Use Only.

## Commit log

2025-08-13 Init commit
    [01-013 robot_mount_fixed.SLDPRT, 6900 BALEKA II .SLDASM, AK10-9 KV60 V3.0.SLDPRT, AssemblyFootV2 BALEKA II .SLDASM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]
2025-08-30 Completed Assembly guide
    Made some stylistic changes to the model while completing the assembly guide
    [6900 BALEKA II .SLDASM, AssemblyFootV2 BALEKA II .SLDASM, BLK001-top_plate.SLDPRT, BLKS-P011-Back_plate_spacer.SLDPRT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]
